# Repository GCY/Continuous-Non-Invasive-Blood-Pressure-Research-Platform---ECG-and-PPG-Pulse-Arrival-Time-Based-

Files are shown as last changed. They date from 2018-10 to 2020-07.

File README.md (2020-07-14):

# Continuous Non-Invasive Blood Pressure Research Platform - ECG and PPG Pulse Arrival Time Based
This project is cuffless cNIBP research platform with ECG(two-electrode, without Right Leg Drive(RLD) ) and PPG(MAX3010x),  the Pulse Arrival Time (PAT) using ECG and PPG signal, measure the time delay(∆t) between QRS-Complex of the ECG signal and any one systolic peak of the PPG signal.

<p align="center">
 
</p>

## Hardware

### V4

coming soon...

- STM32F405
- ECG : INA333+AD8669(without RLD)
- Electrode : PCB Pads and NeuroSky EEG dry 6mm electrode(Pinhole PAD1 & PAD2) [NeuroSky](http://neurosky.com)
- PPG : LArm
- LCM : 128x64 SSD1306
- OUTPUT : USB-FS VCP
- Charger : BQ24014

### V3

- STM32F405
- ECG : INA827+LM324PWR(without RLD)
- Electrode : PCB Pads and NeuroSky EEG dry 6mm electrode(Pinhole PAD1 & PAD2) [NeuroSky](http://neurosky.com)
- PPG : LArm
- LCM : 128x64 SSD1306
- OUTPUT : USB-FS VCP
- Charger : TP4056*

#### Note
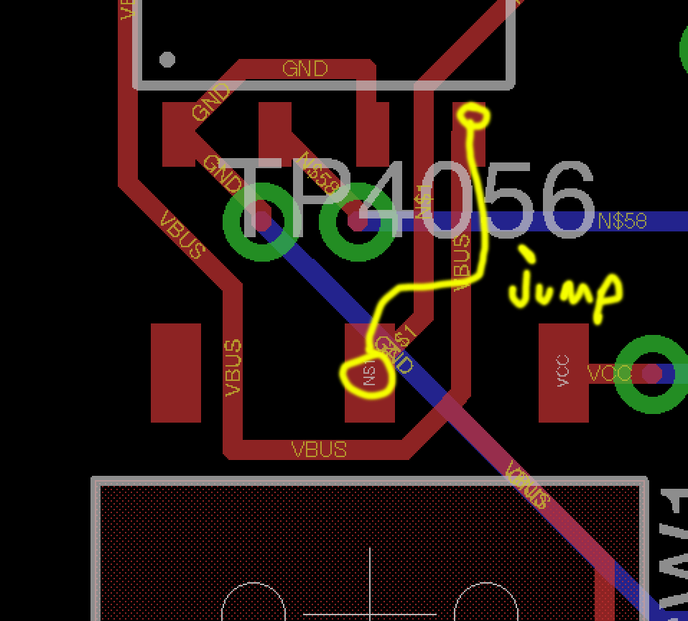
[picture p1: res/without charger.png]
- TP4056 have mV level peak-to-peak noise... so, jump VBUS to switch... 
- Replace D1 to 0R resistor, reduce LDO VDDA noise.
- Unplug the NB AC adapter.

</br>



### V1
- STM32F407
- ECG : INA827+LM324PWR(without RLD)
- Electrode : PCB Pads
- PPG : LArm and RArm
- LCM : 128x64 SSD1306
- OUTPUT : UART

## Firmware
This firmware only for testing, includes USB-FS VCP, Max3010x Spo2 algorithm, PPG and ECG signal oscilloscope display.</br>

 - cd ./firmware/stm32f405/src/
 - make
 - load elf file
 - run
## Software
[wxECGAnalyzer](https://github.com/GCY/wxECGAnalyzer) is a QRS-Complex ECG signal process tool and QRS-Complex detection algorithm validation tools, [Pulse Oximeter MAX3010X](https://github.com/GCY/Pulse-Oximeter-with-MAX3010X) is a Spo2 signal process and r-ratio finetune tool, combining the two tools, could implement the PAT-BP regression algorithm.

</br>

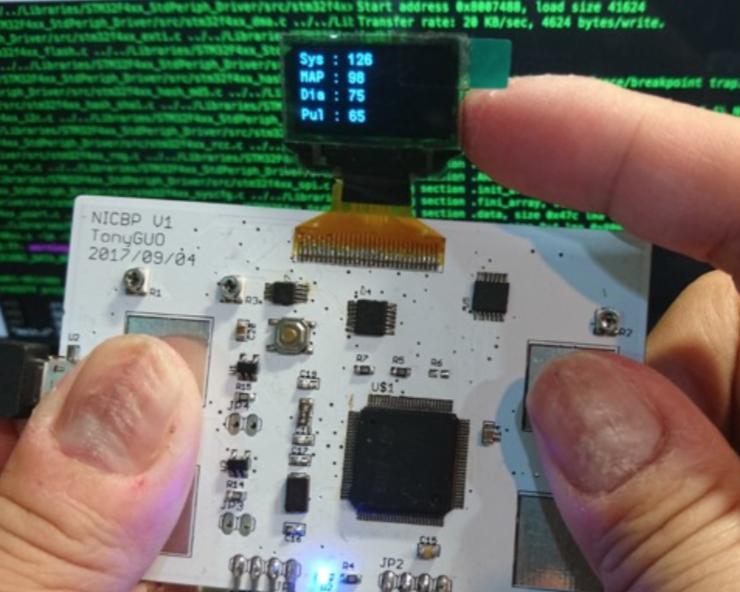
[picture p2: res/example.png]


## Pulse Arrival Time Calculate

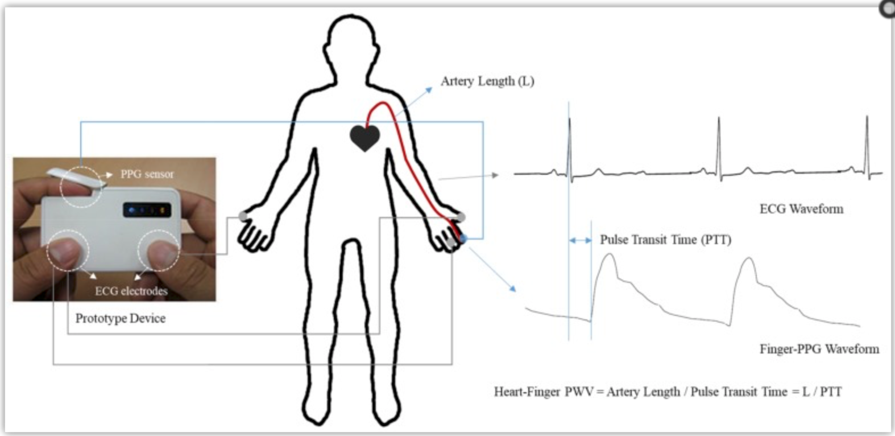
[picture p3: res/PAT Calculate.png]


## What's cuff-less blood pressure monitor and difference between Pulse Arrival Time(PAT) and Pulse Transit Time(PTT)
In cuffless non-invasive blood pressure monitor field, we with the accurate calibration of PAT to BP, beat-to-beat BP can be estimated from PAT. On the basis of the theoretical relationship between PAT and BP and their experimental or empirical relationship, various models that correlate PAT with BP have been established.</br>
</br>
PAT and BP with Regression: </br>
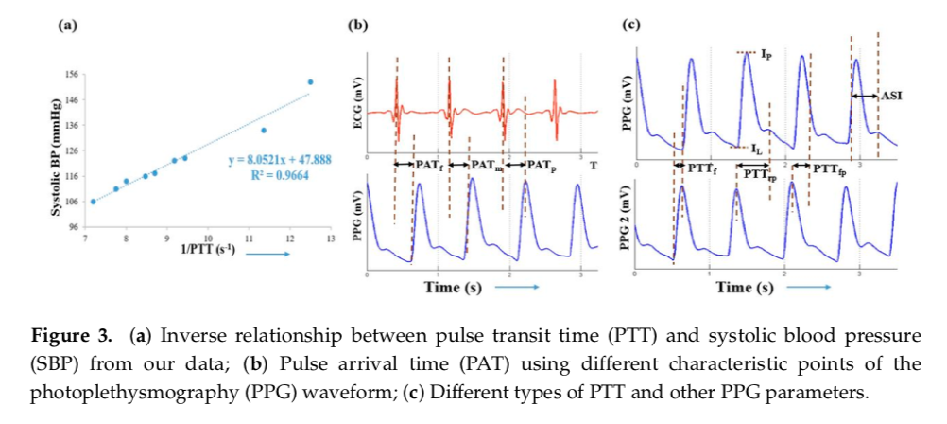
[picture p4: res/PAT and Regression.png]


</br>
</br>
Pulse transit time (PTT) is the time it takes for the pressure or flow wave to propagate between two arterial sites.
PTT measured as the time delay between invasive proximal and distal blood pressure or flow, and PTT(propagate time) can be converted to Pulse Wave Velocity(PWV is speed unit).

the most used is the R-wave(QRS Complex) in the electrocardiogram (ECG) and combine pulsemeter(piezo or PPG), leading to the so called pulse arrival time (PAT). 
PAT is not exactly the PTT, as it includes the time interval between ventricular depolarization and the opening of the aortic valve which is known as pre-ejection period (PEP) and it varies beat-to-beat.

Most efforts have employed the time delay between ECG and finger photoplethysmography (PPG) waveforms as a convenient surrogate of PTT. 

However, these conventional pulse arrival time (PAT) measurements include the pre-ejection period (PEP) and the time delay through small,
muscular arteries and may thus be an unreliable marker of BP.

Shortcoming is that PAT includes the pre-ejection period (PEP) in addition to PTT. 
Since the PEP component depends on the electromechanical functioning of the heart, it can change independently of PTT and thus BP. 

Because the ECG QRS-Complex is not the starting point for blood to actually enter the radial artery, it is a biopotential to depolarization of the sinus node

</br>

## This project only for research

</br>

(https://www.youtube.com/watch?v=RtydQm8okKk)

</br>

## Reference :
- [1] Continuous Blood Pressure Measurement from Invasive to Unobtrusive: Celebration of 200th Birth Anniversary of Carl Ludwig</br>
- [2] Cuff-Less and Continuous Blood Pressure Monitoring: A Methodological Review</br>
- [3] https://www.egr.msu.edu/classes/ece480/capstone/spring13/group03/documents.html
- [4] Cho, J., & Baek, H. J. (2020). A Comparative Study of Brachial–Ankle Pulse Wave Velocity and Heart–Finger Pulse Wave Velocity in Korean Adults. Sensors, 20(7), 2073.
 
LICENSE
-------

MIT License

Copyright (c) 2020 Tony Guo

Permission is hereby granted, free of charge, to any person obtaining a copy
of this software and associated documentation files (the "Software"), to deal
in the Software without restriction, including without limitation the rights
to use, copy, modify, merge, publish, distribute, sublicense, and/or sell
copies of the Software, and to permit persons to whom the Software is
furnished to do so, subject to the following conditions:

The above copyright notice and this permission notice shall be included in all
copies or substantial portions of the Software.

THE SOFTWARE IS PROVIDED "AS IS", WITHOUT WARRANTY OF ANY KIND, EXPRESS OR
IMPLIED, INCLUDING BUT NOT LIMITED TO THE WARRANTIES OF MERCHANTABILITY,
FITNESS FOR A PARTICULAR PURPOSE AND NONINFRINGEMENT. IN NO EVENT SHALL THE
AUTHORS OR COPYRIGHT HOLDERS BE LIABLE FOR ANY CLAIM, DAMAGES OR OTHER
LIABILITY, WHETHER IN AN ACTION OF CONTRACT, TORT OR OTHERWISE, ARISING FROM,
OUT OF OR IN CONNECTION WITH THE SOFTWARE OR THE USE OR OTHER DEALINGS IN THE
SOFTWARE.

OSHW Certification
-------

https://certification.oshwa.org/tw000003.html

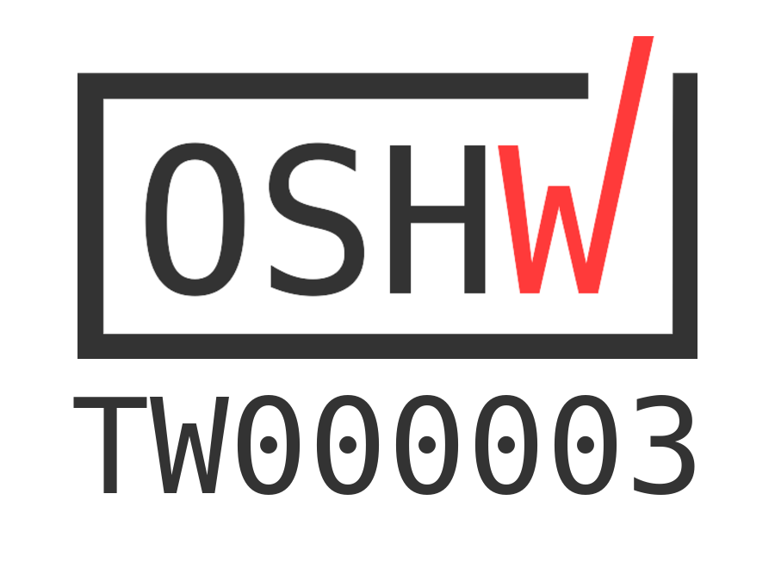
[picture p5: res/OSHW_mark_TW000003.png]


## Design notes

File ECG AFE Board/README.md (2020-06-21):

# ECG Analog-Front-End Design

two electrode ECG without RLD

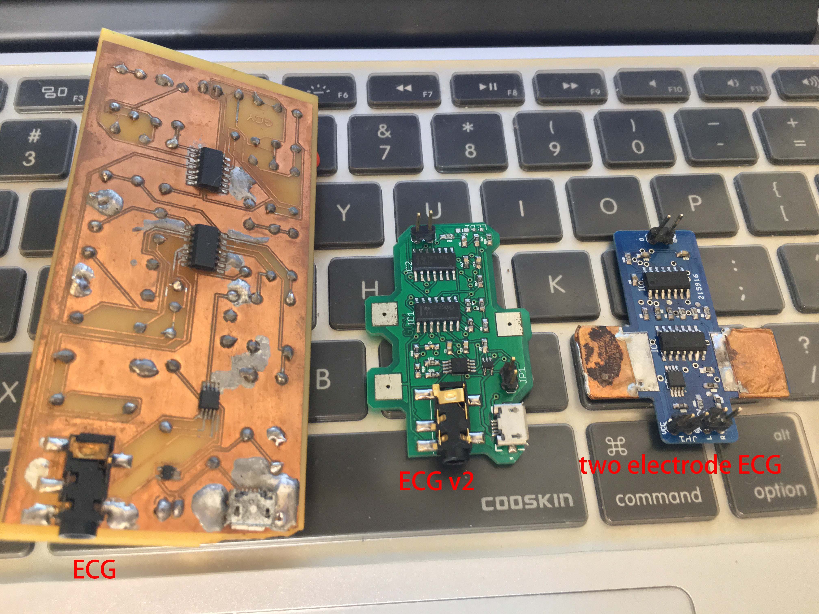
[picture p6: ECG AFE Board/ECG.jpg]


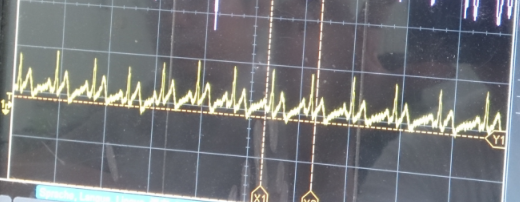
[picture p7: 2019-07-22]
res/ecg osc.png

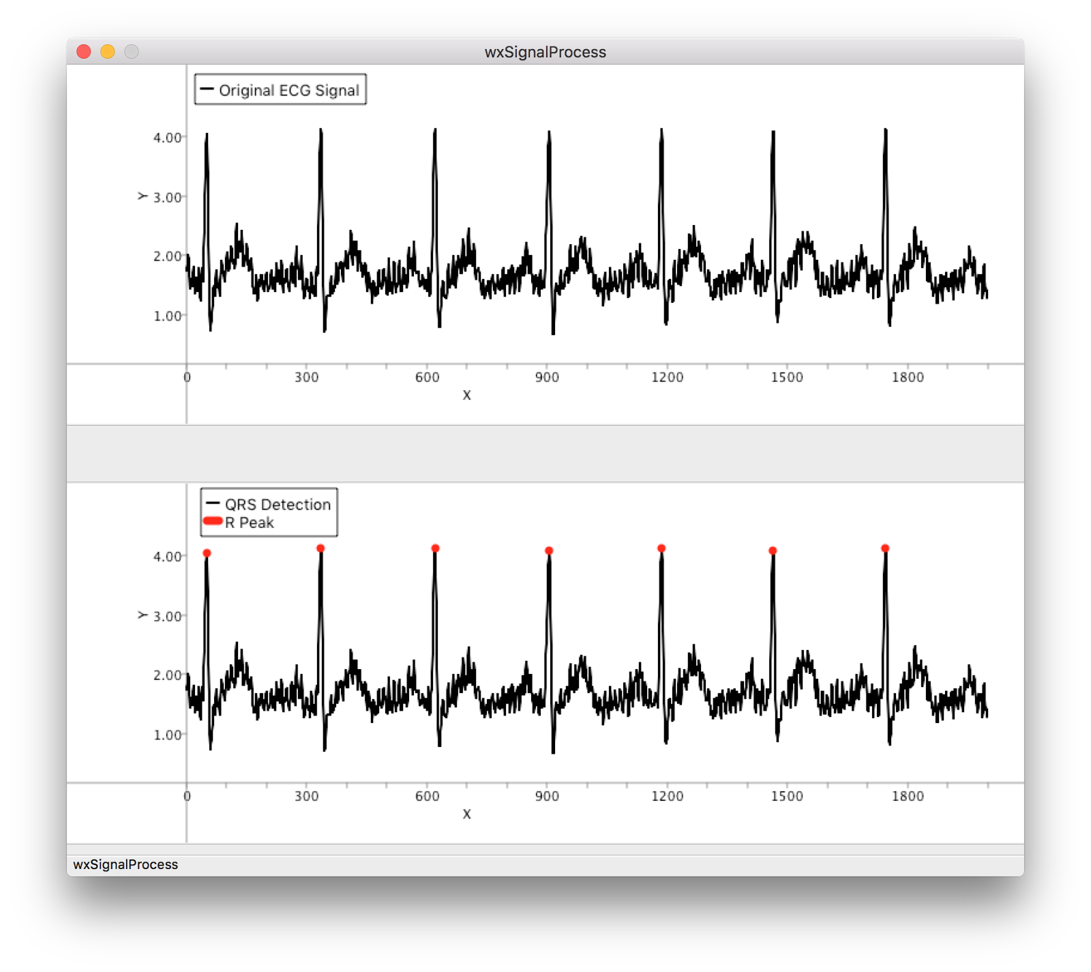
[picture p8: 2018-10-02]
res/QRS Complex Detect.png

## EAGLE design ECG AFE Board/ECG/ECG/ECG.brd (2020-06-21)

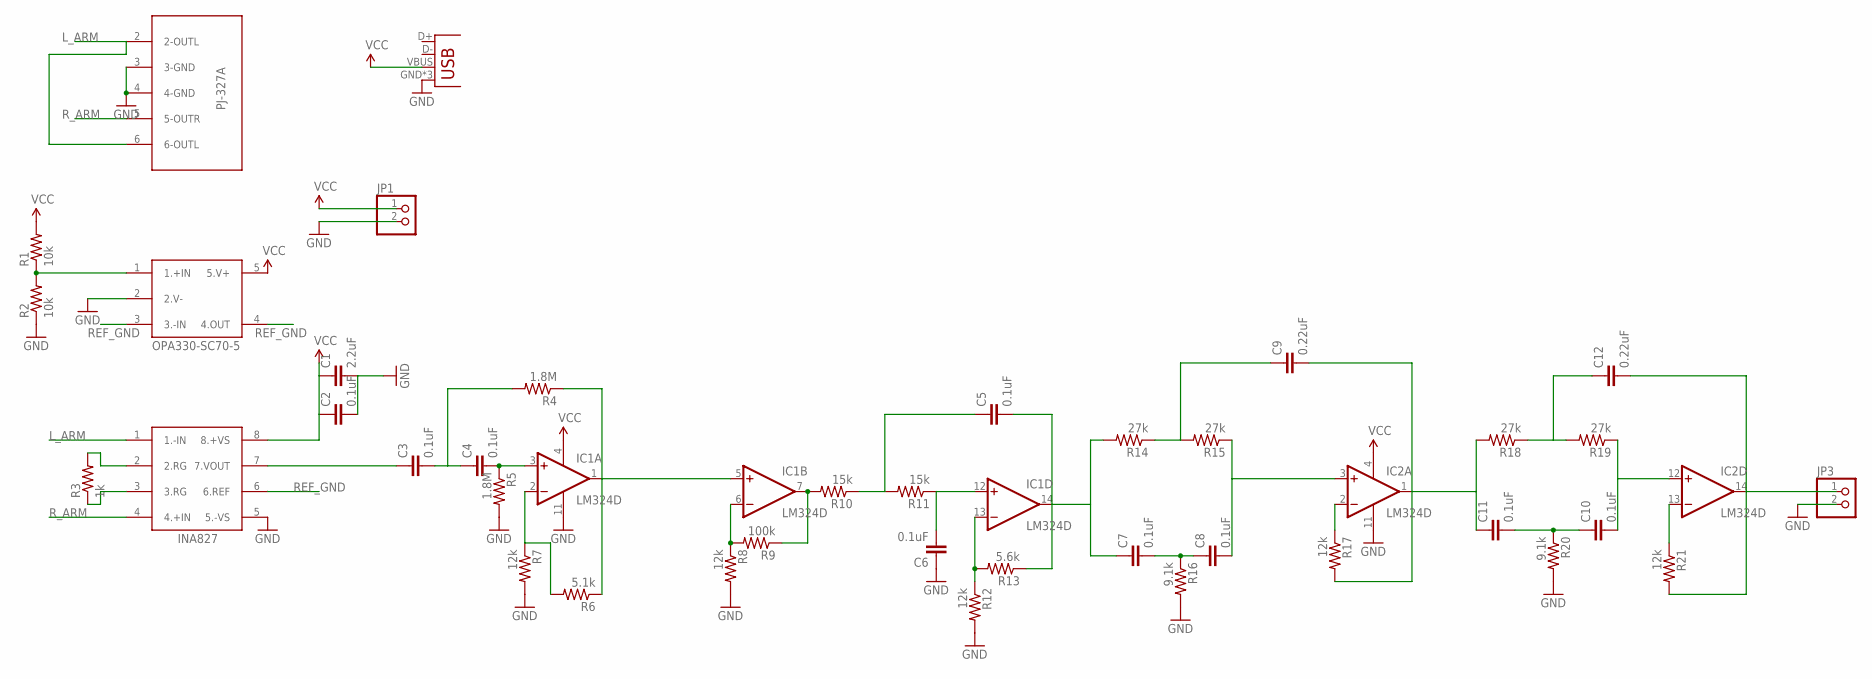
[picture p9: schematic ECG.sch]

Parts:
C1: 2.2uF; CAP-PTH-LARGE
C2, C3, C4, C5, C6, C7, C8, C10, C11: 0.1uF; CAP-PTH-LARGE
C9, C12: 0.22uF; CAP-PTH-LARGE
IC1, IC2: LM324D; SO14
JP1, JP3: PINHD-1X2; 1X02
JP2: USB-MICROB
R1, R2: 10k; AXIAL-0.4
R3: 1k; AXIAL-0.4
R4, R5: 1.8M; AXIAL-0.4
R6: 5.1k; AXIAL-0.4
R7, R8, R12, R17, R21: 12k; AXIAL-0.4
R9: 100k; AXIAL-0.4
R10, R11: 15k; AXIAL-0.4
R13: 5.6k; AXIAL-0.4
R14, R15, R18, R19: 27k; AXIAL-0.4
R16, R20: 9.1k; AXIAL-0.4
U$1: OPA330-SC70-5
U$2: INA827
U$3: PJ-327A

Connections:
GND: C1.2, C2.2, C6.1, IC1.11 (V-), IC2.11 (V-), JP1.2, JP2.GND, JP2.MT1 (GND), JP2.MT2 (GND), JP3.2, R2.P$1 (1), R5.P$2 (2), R7.P$2 (2), R8.P$2 (2), R12.P$2 (2), R16.P$2 (2), R20.P$2 (2), U$1.2 (2.V-), U$2.5 (5.-VS), U$3.3 (3-GND), U$3.4 (4-GND)
L_ARM: U$2.1 (1.-IN), U$3.2 (2-OUTL), U$3.6 (6-OUTL)
unnamed: R1.P$1 (1), R2.P$2 (2), U$1.1 (1.+IN)
unnamed: R3.P$2 (2), U$2.2 (2.RG)
unnamed: R3.P$1 (1), U$2.3 (3.RG)
unnamed: C4.2, IC1.3 (+IN), R5.P$1 (1)
unnamed: C3.1, U$2.7 (7.VOUT)
unnamed: C3.2, C4.1, R4.P$2 (2)
unnamed: IC1.1 (OUT), IC1.5 (+IN), R4.P$1 (1), R6.P$1 (1)
unnamed: IC1.2 (-IN), R6.P$2 (2), R7.P$1 (1)
unnamed: C5.1, R10.P$1 (1), R11.P$2 (2)
unnamed: IC1.6 (-IN), R8.P$1 (1), R9.P$2 (2)
unnamed: IC1.7 (OUT), R9.P$1 (1), R10.P$2 (2)
unnamed: C6.2, IC1.12 (+IN), R11.P$1 (1)
unnamed: C5.2, C7.1, IC1.14 (OUT), R13.P$1 (1), R14.P$2 (2)
unnamed: IC1.13 (-IN), R12.P$1 (1), R13.P$2 (2)
unnamed: C9.1, R14.P$1 (1), R15.P$2 (2)
unnamed: C8.2, IC2.3 (+IN), R15.P$1 (1)
unnamed: C7.2, C8.1, R16.P$1 (1)
unnamed: IC2.2 (-IN), R17.P$1 (1)
unnamed: C9.2, C11.1, IC2.1 (OUT), R17.P$2 (2), R18.P$2 (2)
unnamed: IC2.13 (-IN), R21.P$1 (1)
unnamed: C10.1, C11.2, R20.P$1 (1)
unnamed: C10.2, IC2.12 (+IN), R19.P$1 (1)
unnamed: C12.1, R18.P$1 (1), R19.P$2 (2)
unnamed: C12.2, IC2.14 (OUT), JP3.1, R21.P$2 (2)
REF_GND: U$1.3 (3.-IN), U$1.4 (4.OUT), U$2.6 (6.REF)
R_ARM: U$2.4 (4.+IN), U$3.5 (5-OUTR)
VCC: C1.1, C2.1, IC1.4 (V+), IC2.4 (V+), JP1.1, JP2.VBUS, R1.P$2 (2), U$1.5 (5.V+), U$2.8 (8.+VS)

Board: 2 copper layers, 41 parts (0 on the bottom side), 29 nets, no tracks yet.

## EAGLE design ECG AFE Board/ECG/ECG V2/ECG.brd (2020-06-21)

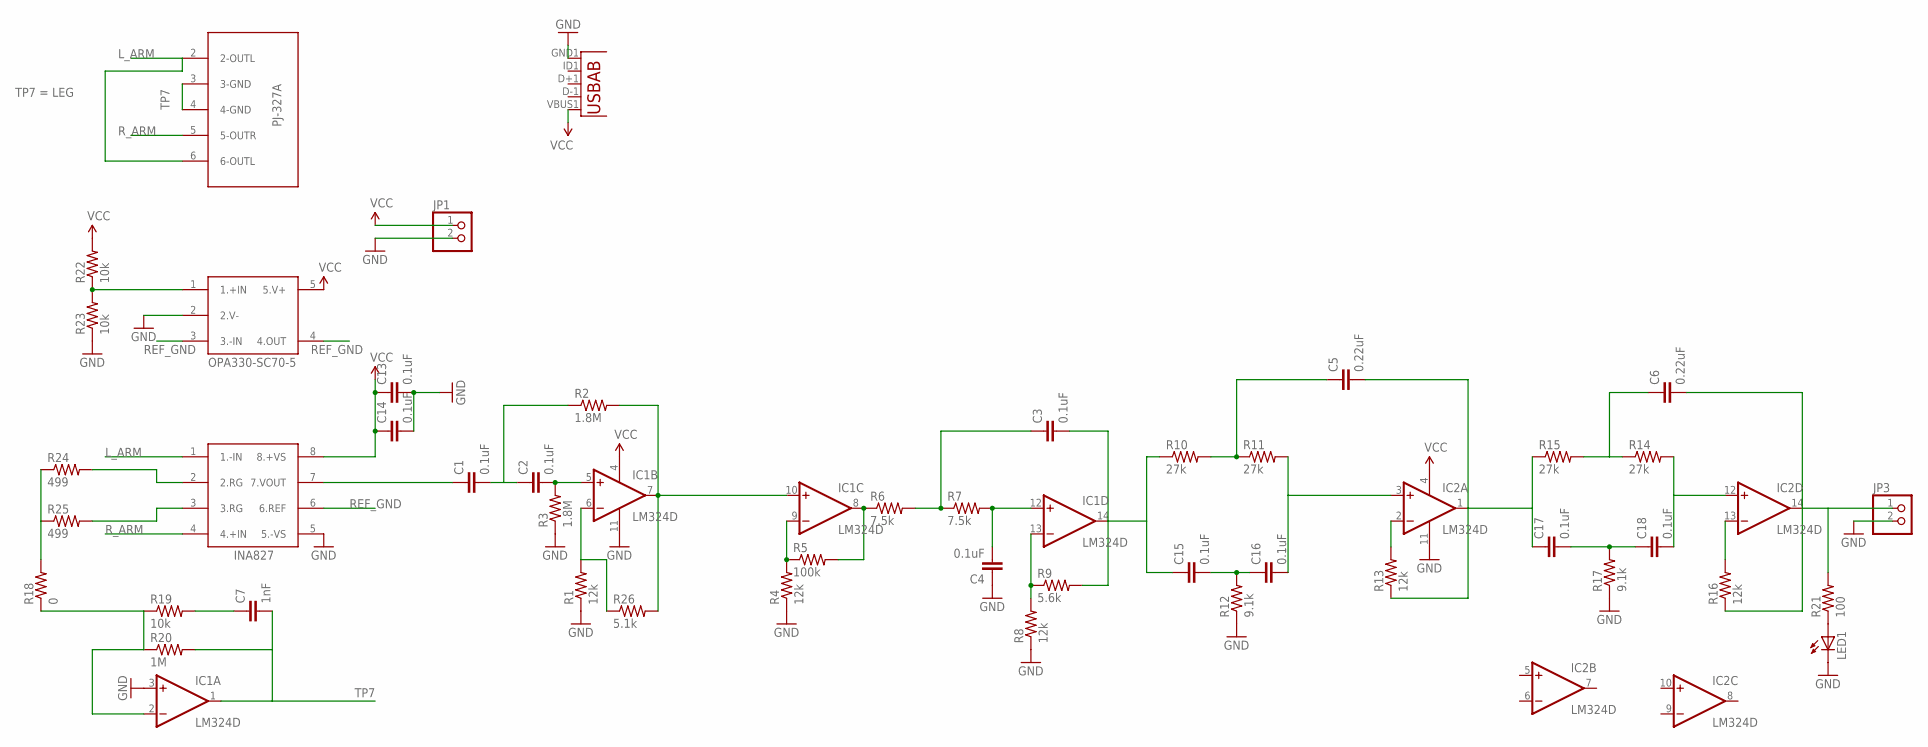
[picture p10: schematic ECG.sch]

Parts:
C1, C2, C3, C4, C13, C14, C15, C16, C17, C18: 0.1uF; 0603-CAP
C5, C6: 0.22uF; 0603-CAP
C7: 1nF; 0603-CAP
IC1, IC2: LM324D; SO14
JP1, JP3: PINHD-1X2; 1X02
LED1: LEDCHIPLED_0603; CHIPLED_0603
R1, R4, R8, R13, R16: 12k; 0603-RES
R2, R3: 1.8M; 0603-RES
R5: 100k; 0603-RES
R6, R7: 7.5k; 0603-RES
R9: 5.6k; 0603-RES
R10, R11, R14, R15: 27k; 0603-RES
R12, R17: 9.1k; 0603-RES
R18: 0; 0603-RES
R19, R22, R23: 10k; 0603-RES
R20: 1M; 0603-RES
R21: 100; 0603-RES
R24, R25: 499; 0603-RES
R26: 5.1k; 0603-RES
U1: USB""; USB-MICRO-SMD
U$1: OPA330-SC70-5
U$2: INA827
U$3: PJ-327A

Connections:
GND: C4.1, C13.2, C14.2, IC1.3 (+IN), IC1.11 (V-), IC2.11 (V-), JP1.2, JP3.2, LED1.C, R1.1, R3.1, R4.1, R8.1, R12.1, R17.1, R23.1, U1.GND1 (GND), U$1.2 (2.V-), U$2.5 (5.-VS)
L_ARM: U$2.1 (1.-IN), U$3.2 (2-OUTL), U$3.6 (6-OUTL)
unnamed: R22.1, R23.2, U$1.1 (1.+IN)
unnamed: R24.2, U$2.2 (2.RG)
unnamed: R25.2, U$2.3 (3.RG)
unnamed: C2.2, IC1.5 (+IN), R3.2
unnamed: C1.1, U$2.7 (7.VOUT)
unnamed: C1.2, C2.1, R2.1
unnamed: IC1.7 (OUT), IC1.10 (+IN), R2.2, R26.2
unnamed: IC1.6 (-IN), R1.2, R26.1
unnamed: C3.1, R6.2, R7.1
unnamed: IC1.9 (-IN), R4.2, R5.1
unnamed: IC1.8 (OUT), R5.2, R6.1
unnamed: C4.2, IC1.12 (+IN), R7.2
unnamed: C3.2, C15.1, IC1.14 (OUT), R9.2, R10.1
unnamed: IC1.13 (-IN), R8.2, R9.1
unnamed: C5.1, R10.2, R11.1
unnamed: C16.2, IC2.3 (+IN), R11.2
unnamed: C15.2, C16.1, R12.2
unnamed: IC2.2 (-IN), R13.2
unnamed: C5.2, C17.1, IC2.1 (OUT), R13.1, R15.1
unnamed: IC2.13 (-IN), R16.2
unnamed: C17.2, C18.1, R17.2
unnamed: C18.2, IC2.12 (+IN), R14.2
unnamed: C6.1, R14.1, R15.2
unnamed: C6.2, IC2.14 (OUT), JP3.1, R16.1, R21.2
unnamed: R18.2, R24.1, R25.1
unnamed: IC1.2 (-IN), R18.1, R19.1, R20.1
unnamed: C7.1, R19.2
unnamed: LED1.A, R21.1
REF_GND: U$1.3 (3.-IN), U$1.4 (4.OUT), U$2.6 (6.REF)
R_ARM: U$2.4 (4.+IN), U$3.5 (5-OUTR)
TP7: C7.2, IC1.1 (OUT), R20.2, U$3.3 (3-GND), U$3.4 (4-GND)
VCC: C13.1, C14.1, IC1.4 (V+), IC2.4 (V+), JP1.1, R22.2, U1.VBUS1 (VBUS), U$1.5 (5.V+), U$2.8 (8.+VS)

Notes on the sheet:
TP7 = LEG

Board: 2 copper layers, 48 parts (19 on the bottom side), 34 nets, no tracks yet.

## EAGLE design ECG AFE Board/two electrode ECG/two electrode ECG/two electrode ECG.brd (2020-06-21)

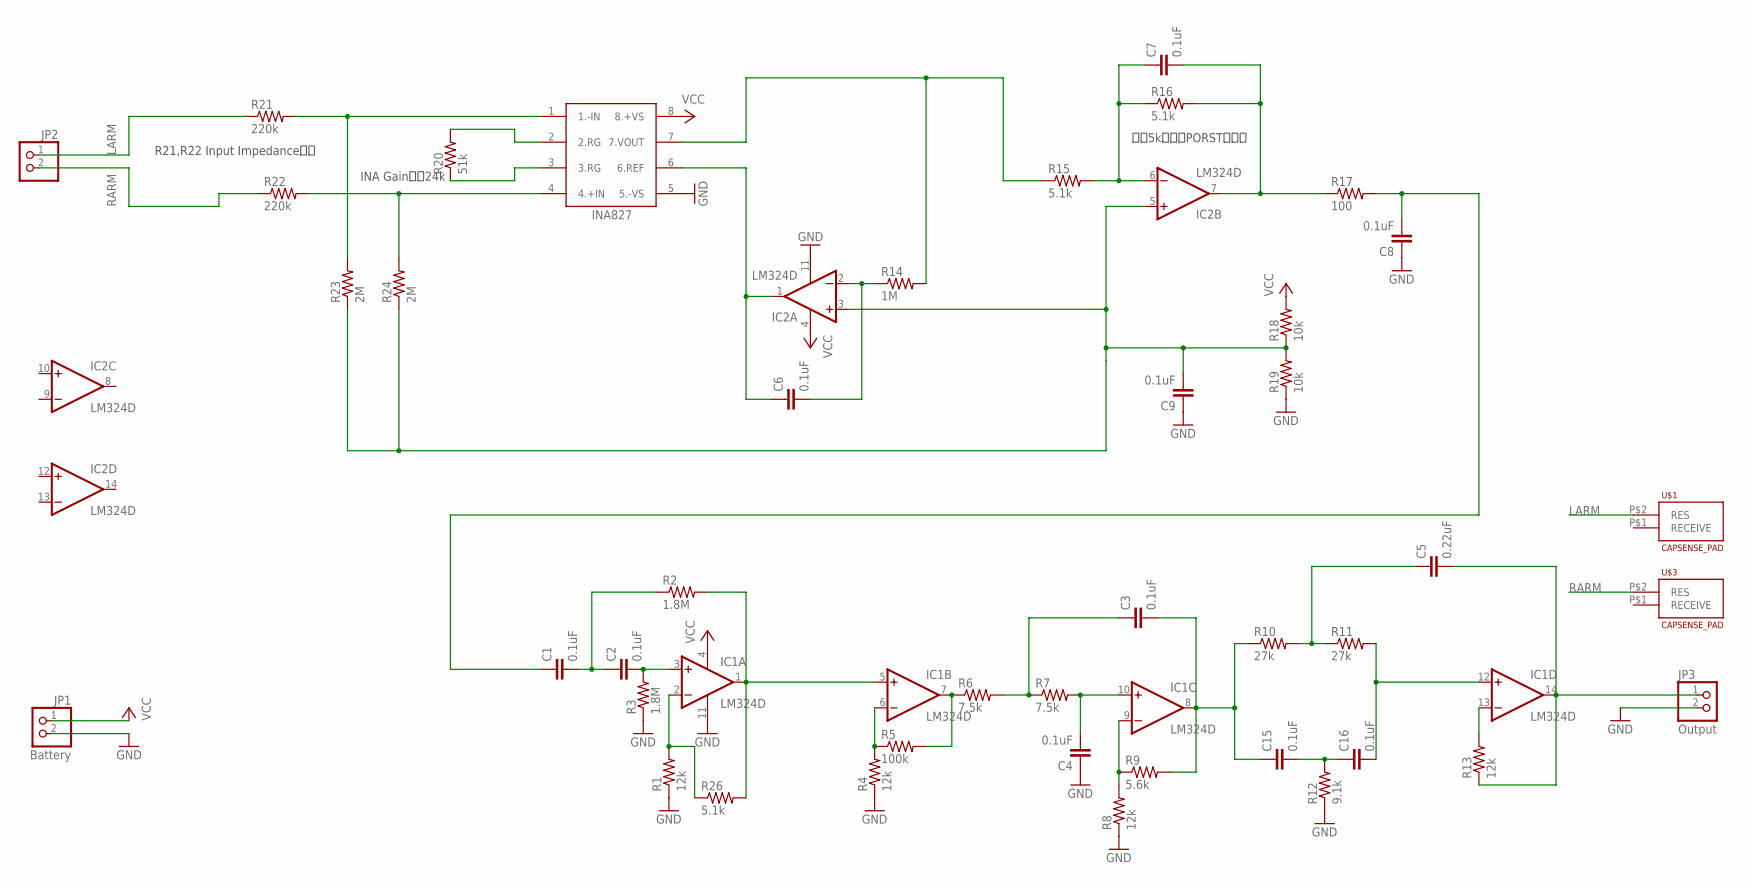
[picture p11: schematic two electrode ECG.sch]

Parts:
C1, C2, C3, C4, C6, C7, C8, C9, C15, C16: 0.1uF; 0603-CAP
C5: 0.22uF; 0603-CAP
IC1, IC2: LM324D; SO14
JP1: Battery; 1X02
JP2: PINHD-1X2; 1X02
JP3: Output; 1X02
R1, R4, R8, R13: 12k; 0603-RES
R2, R3: 1.8M; 0603-RES
R5: 100k; 0603-RES
R6, R7: 7.5k; 0603-RES
R9: 5.6k; 0603-RES
R10, R11: 27k; 0603-RES
R12: 9.1k; 0603-RES
R14: 1M; 0603-RES
R15, R16, R26: 5.1k; 0603-RES
R17: 100; 0603-RES
R18, R19: 10k; 0603-RES
R20: 51k; 0603-RES
R21, R22: 220k; 0603-RES
R23, R24: 2M; 0603-RES
U$1, U$3: CAPSENSE_PAD
U$2: INA827

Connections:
GND: C4.1, C8.1, C9.1, IC1.11 (V-), IC2.11 (V-), JP1.2, JP3.2, R1.1, R3.1, R4.1, R8.1, R12.1, R19.1, U$2.5 (5.-VS)
LARM: JP2.1, R21.1, U$1.P$2 (RES)
unnamed: R20.2, U$2.2 (2.RG)
unnamed: C6.2, IC2.2 (-IN), R14.1
unnamed: R14.2, R15.1, U$2.7 (7.VOUT)
unnamed: C2.2, IC1.3 (+IN), R3.2
unnamed: R21.2, R23.2, U$2.1 (1.-IN)
unnamed: C1.2, C2.1, R2.1
unnamed: IC1.1 (OUT), IC1.5 (+IN), R2.2, R26.2
unnamed: IC1.2 (-IN), R1.2, R26.1
unnamed: C3.1, R6.2, R7.1
unnamed: IC1.6 (-IN), R4.2, R5.1
unnamed: IC1.7 (OUT), R5.2, R6.1
unnamed: C4.2, IC1.10 (+IN), R7.2
unnamed: C3.2, C15.1, IC1.8 (OUT), R9.2, R10.1
unnamed: IC1.9 (-IN), R8.2, R9.1
unnamed: C5.1, R10.2, R11.1
unnamed: C16.2, IC1.12 (+IN), R11.2
unnamed: C15.2, C16.1, R12.2
unnamed: IC1.13 (-IN), R13.2
unnamed: C5.2, IC1.14 (OUT), JP3.1, R13.1
unnamed: C6.1, IC2.1 (OUT), U$2.6 (6.REF)
unnamed: C7.1, IC2.6 (-IN), R15.2, R16.1
unnamed: C7.2, IC2.7 (OUT), R16.2, R17.1
unnamed: C1.1, C8.2, R17.2
unnamed: C9.2, IC2.3 (+IN), IC2.5 (+IN), R18.1, R19.2, R23.1, R24.1
unnamed: R20.1, U$2.3 (3.RG)
unnamed: R22.2, R24.2, U$2.4 (4.+IN)
RARM: JP2.2, R22.1, U$3.P$2 (RES)
VCC: IC1.4 (V+), IC2.4 (V+), JP1.1, R18.2, U$2.8 (8.+VS)

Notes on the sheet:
R21,R22 Input Impedance調整
INA Gain調整24k
要改5k，否則PORST會消失

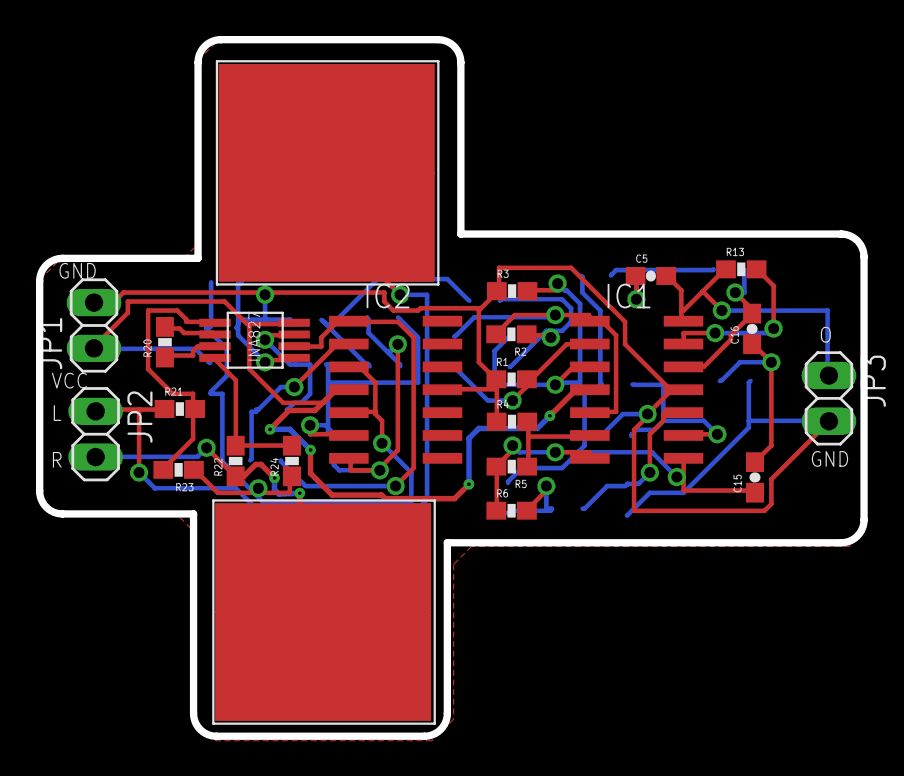
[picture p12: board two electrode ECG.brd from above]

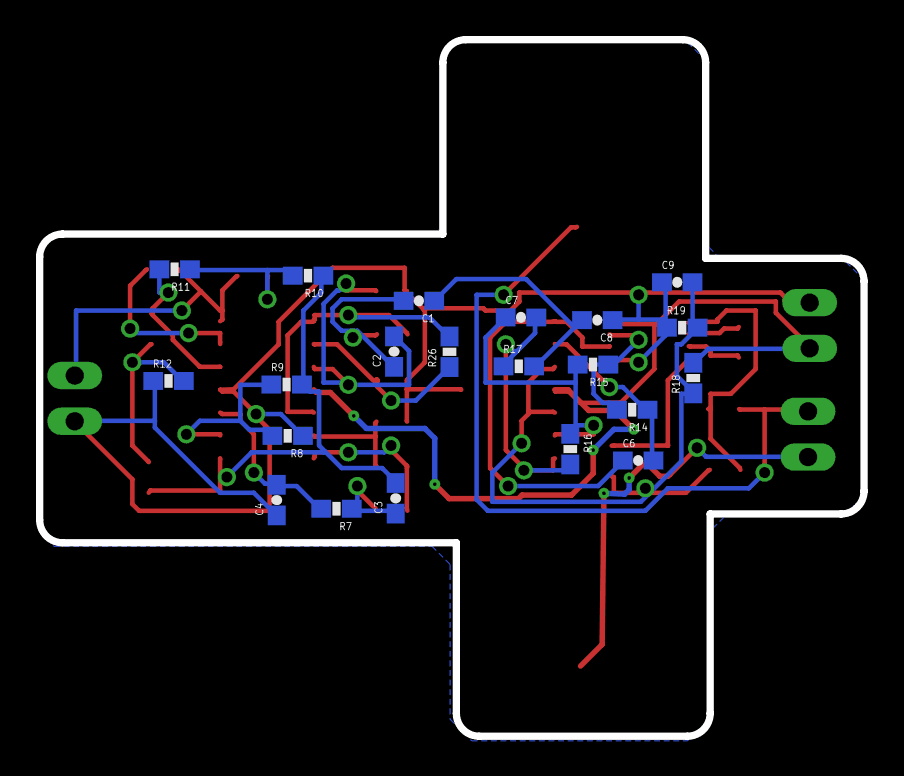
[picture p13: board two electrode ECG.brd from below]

Board: 2 copper layers, 45.8 x 38.7 mm, 44 parts (21 on the bottom side), 30 nets.

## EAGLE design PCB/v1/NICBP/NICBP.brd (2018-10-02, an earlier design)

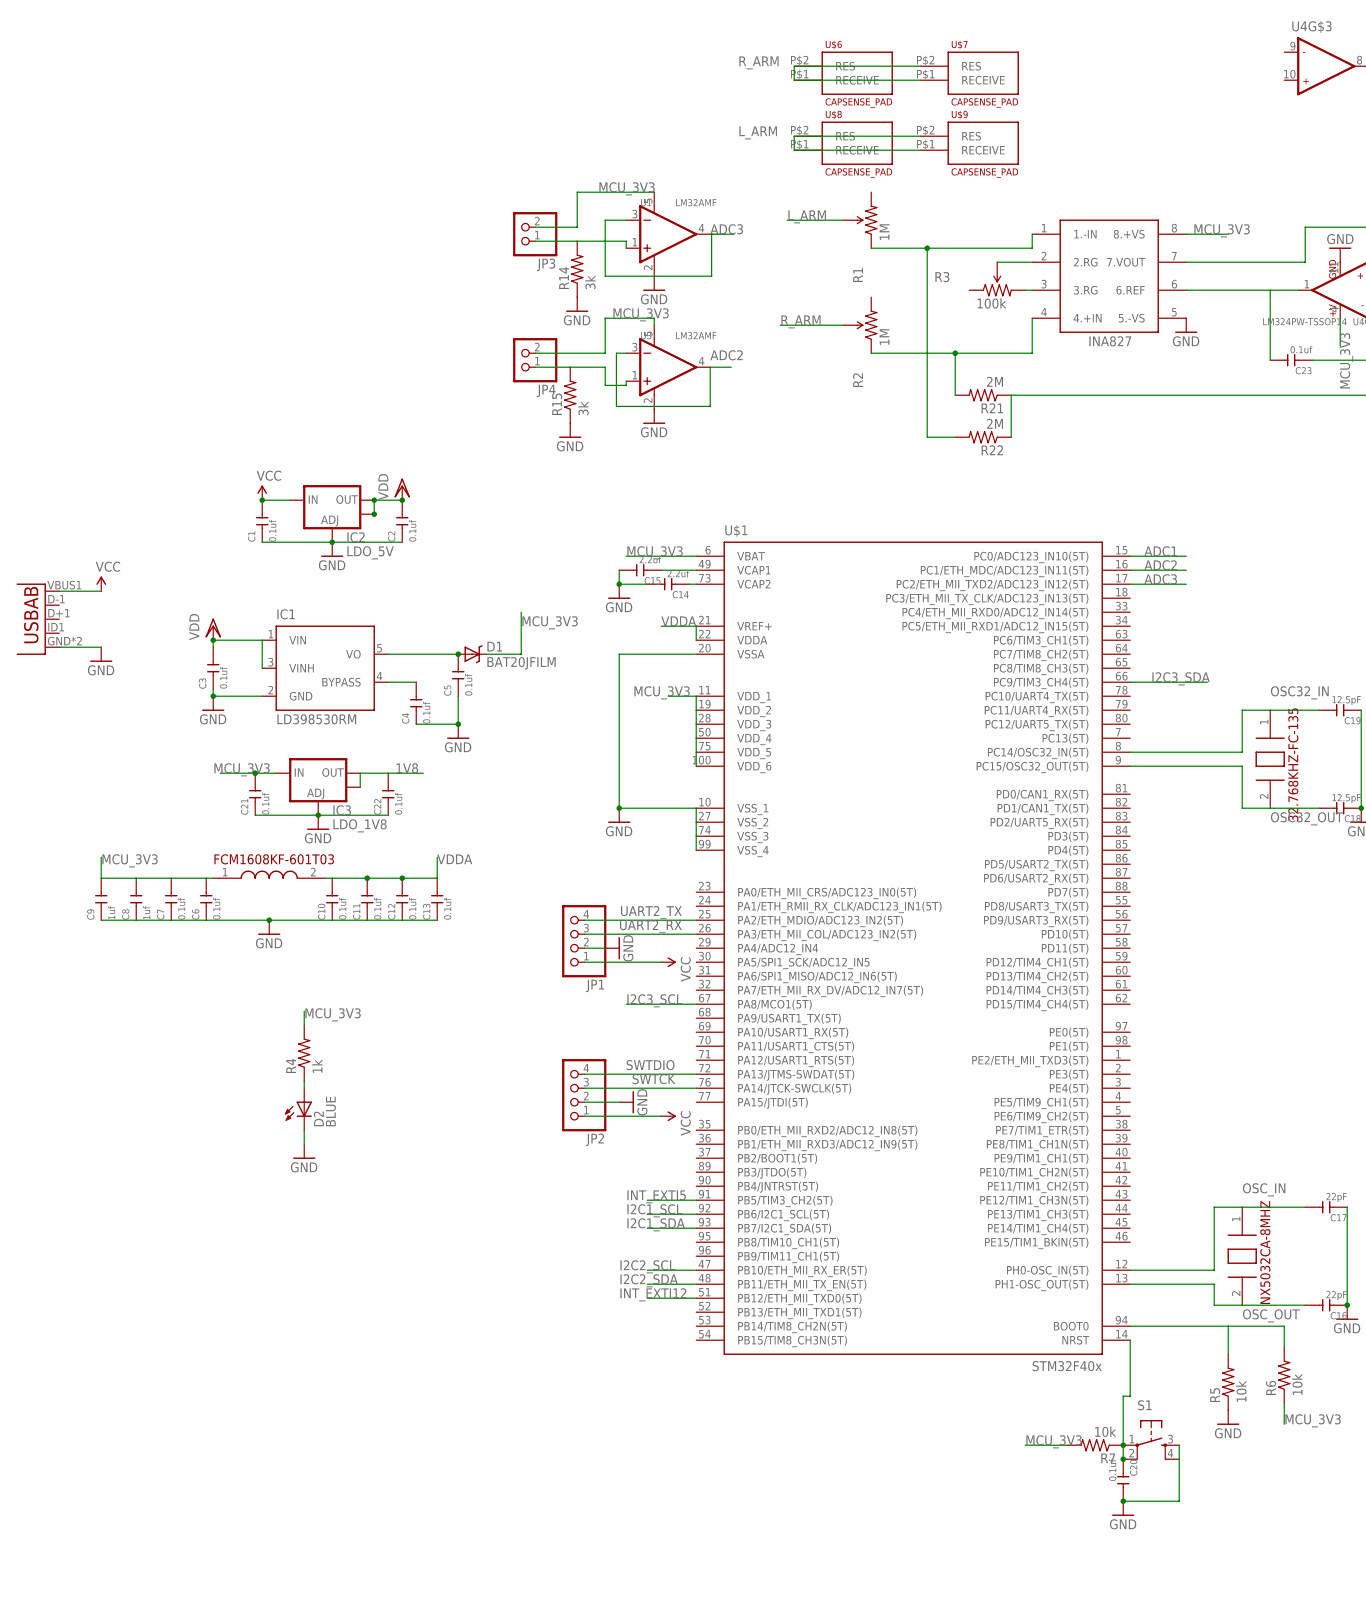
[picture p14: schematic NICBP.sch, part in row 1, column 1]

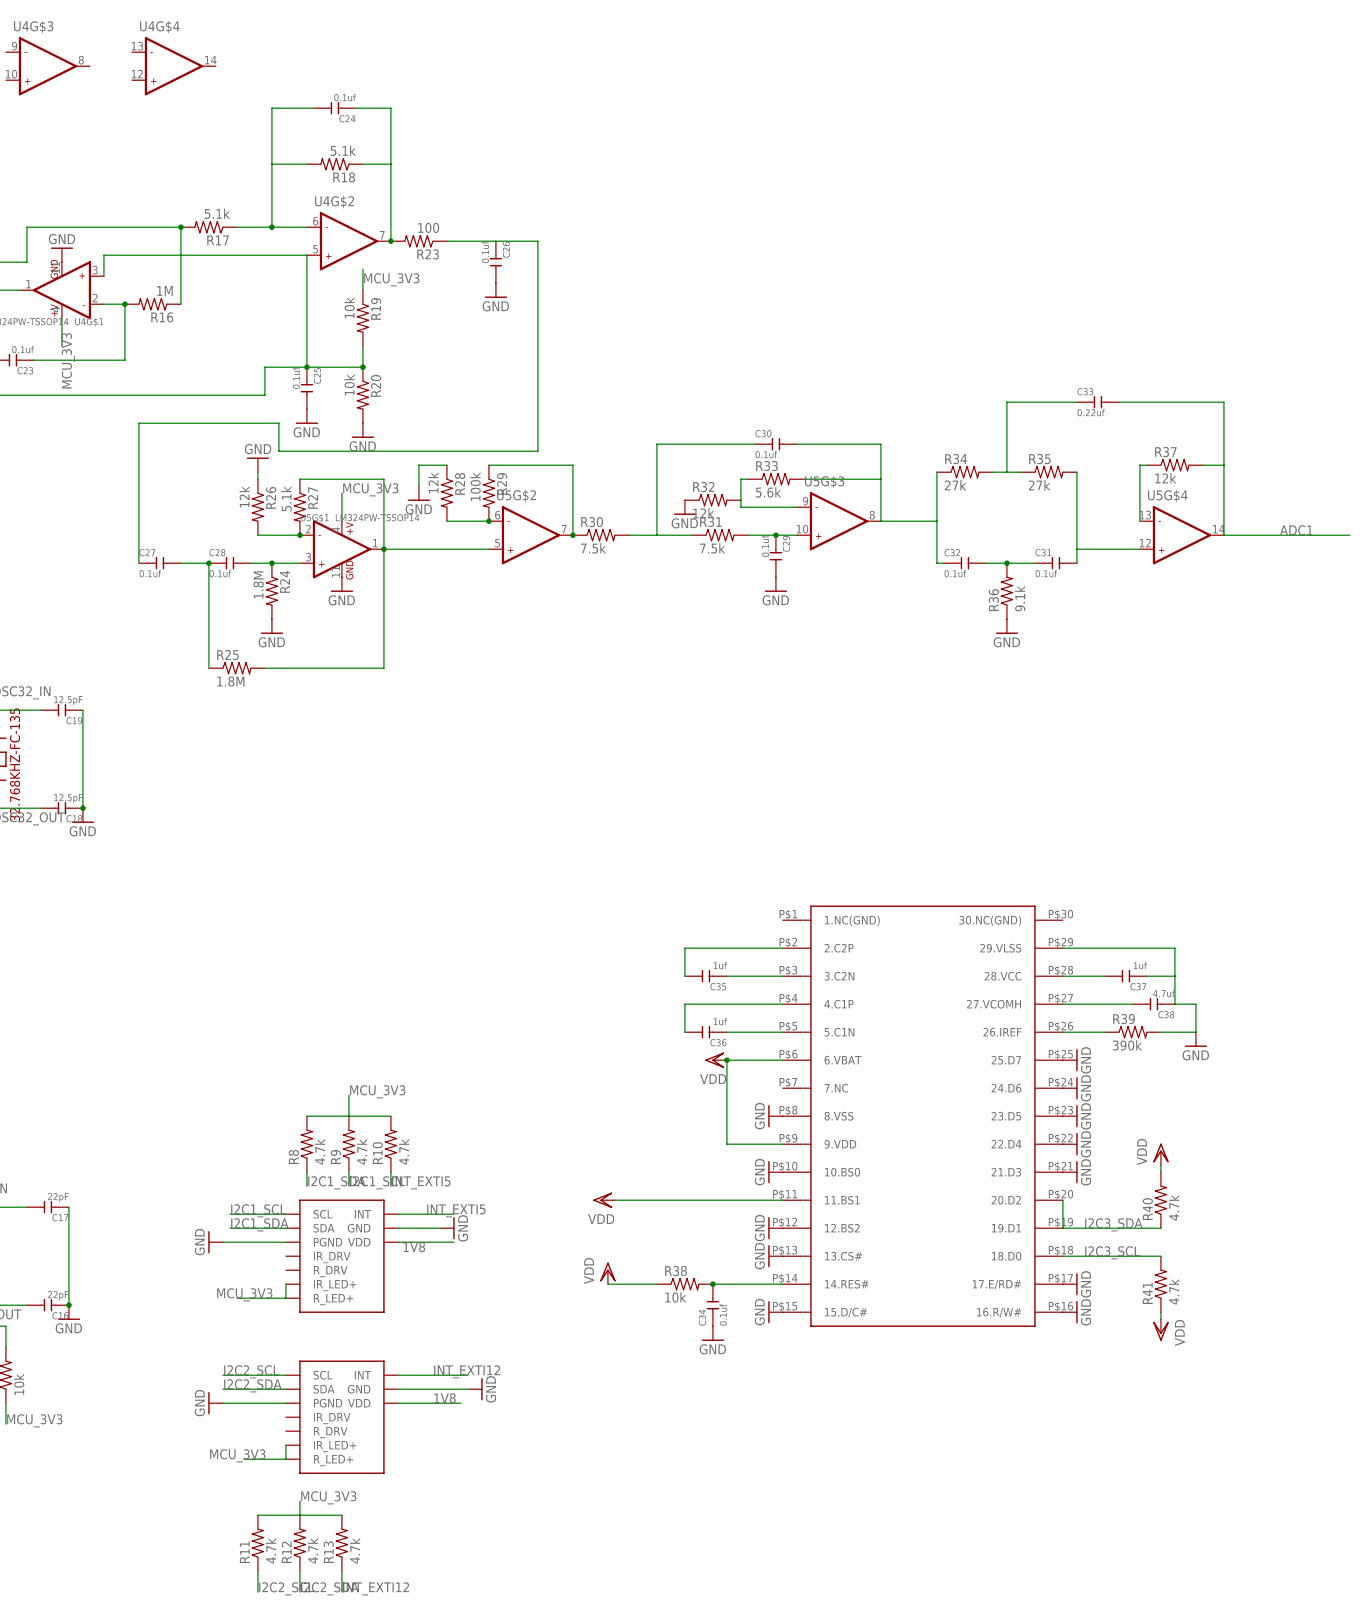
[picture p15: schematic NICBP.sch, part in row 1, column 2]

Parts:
C1, C2, C3, C4, C5, C6, C7, C10, C11, C12, C13, C20, C21, C22, C23, C24, C25, C26, C27, C28, C29, C30, C31, C32, C34: 0.1uf; C0603
C8, C9, C35, C36, C37: 1uf; C0603
C14, C15: 2.2uf; C0603
C16, C17: 22pF; C0603
C18, C19: 12.5pF; C0603
C33: 0.22uf; C0603
C38: 4.7uf; C0603
D1: BAT20JFILM; SOD-323
D2: BLUE; LED-0603
IC1: LD398530RM; SOT23-5L
IC2: LDO_5V; SOT223
IC3: LDO_1V8; SOT223
JP1, JP2: PINHD-1X4; 1X04
JP3, JP4: PINHD-1X2; 1X02
R1, R2: 1M; TRIMPOT_TC33
R3: 100k; TRIMPOT_TC33
R4: 1k; 0603
R5, R6, R7, R19, R20, R38: 10k; 0603
R8, R9, R10, R11, R12, R13, R40, R41: 4.7k; 0603
R14, R15: 3k; 0603
R16: 1M; 0603
R17, R18, R27: 5.1k; 0603
R21, R22: 2M; 0603
R23: 100; 0603
R24, R25: 1.8M; 0603
R26, R28, R32, R37: 12k; 0603
R29: 100k; 0603
R30, R31: 7.5k; 0603
R33: 5.6k; 0603
R34, R35: 27k; 0603
R36: 9.1k; 0603
R39: 390k; 0603
S1: TAC_SWITCHSMD; TACTILE_SWITCH_SMD
U1, U3: LM32AMF; SOT-23-5
U2: USB""; USB-MICRO-SMD
U4, U5: LM324PW-TSSOP14; TSSOP14-0.65-5X4.4MM
U$1: STM32F407V; TQFP100
U$2: NX5032CA-8MHZ
U$3: FCM1608KF-601T03
U$4: 32.768KHZ-FC-135
U$5: INA827
U$6, U$7, U$8, U$9: CAPSENSE_PAD
U$10, U$11: MAX30100
U$12: ER-OLED0.96

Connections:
1V8: C22.2, IC3.2 (OUT), IC3.4 (OUT), U$10.11 (VDD), U$11.11 (VDD)
ADC1: C33.2, R37.2, U5.14 (OUT2), U$1.15 (PC0/ADC123_IN10(5T))
ADC2: U3.3 (IN-), U3.4 (OUT), U$1.16 (PC1/ETH_MDC/ADC123_IN11(5T))
ADC3: U1.3 (IN-), U1.4 (OUT), U$1.17 (PC2/ETH_MII_TXD2/ADC123_IN12(5T))
GND: C1.1, C2.1, C3.1, C4.1, C5.1, C6.1, C7.1, C8.1, C9.1, C10.1, C11.1, C12.1, C13.1, C14.2, C15.2, C16.1, C17.1, C18.1, C19.1, C20.2, C21.1, C22.1, C25.2, C26.2, C29.2, C34.1, C37.1, C38.1, D2.C, IC1.2 (GND), IC2.1 (ADJ), IC3.1 (ADJ), JP1.2, JP2.2, R5.1, R14.1, R15.1, R20.2, R24.2, R26.1, R28.1, R32.1, R36.1, R39.2, S1.3, S1.4, U1.2 (V-), U2.GND, U2.GND1 (GND), U3.2 (V-), U4.11 (GND), U5.11 (GND), U$1.10 (VSS_1), U$1.20 (VSSA), U$1.27 (VSS_2), U$1.74 (VSS_3), U$1.99 (VSS_4), U$5.5 (5.-VS), U$10.4 (PGND), U$10.12 (GND), U$11.4 (PGND), U$11.12 (GND), U$12.P$8 (8.VSS), U$12.P$10 (10.BS0), U$12.P$12 (12.BS2), U$12.P$13 (13.CS#), U$12.P$15 (15.D/C#), U$12.P$16 (16.R/W#), U$12.P$17 (17.E/RD#), U$12.P$21 (21.D3), U$12.P$22 (22.D4), U$12.P$23 (23.D5), U$12.P$24 (24.D6), U$12.P$25 (25.D7), U$12.P$29 (29.VLSS)
I2C1_SCL: R9.1, U$1.92 (PB6/I2C1_SCL(5T)), U$10.2 (SCL)
I2C1_SDA: R8.1, U$1.93 (PB7/I2C1_SDA(5T)), U$10.3 (SDA)
I2C2_SCL: R11.1, U$1.47 (PB10/ETH_MII_RX_ER(5T)), U$11.2 (SCL)
I2C2_SDA: R12.1, U$1.48 (PB11/ETH_MII_TX_EN(5T)), U$11.3 (SDA)
I2C3_SCL: R41.2, U$1.67 (PA8/MCO1(5T)), U$12.P$18 (18.D0)
I2C3_SDA: R40.1, U$1.66 (PC9/TIM3_CH4(5T)), U$12.P$19 (19.D1), U$12.P$20 (20.D2)
INT_EXTI5: R10.1, U$1.91 (PB5/TIM3_CH2(5T)), U$10.13 (INT)
INT_EXTI12: R13.1, U$1.51 (PB12/ETH_MII_TXD0(5T)), U$11.13 (INT)
L_ARM: R1.2 (WIPER), U$8.P$1 (RECEIVE), U$8.P$2 (RES), U$9.P$1 (RECEIVE), U$9.P$2 (RES)
MCU_3V3: C6.2, C7.2, C8.2, C9.2, C21.2, D1.1 (C), IC3.3 (IN), JP3.2, JP4.2, R4.2, R6.1, R7.2, R8.2, R9.2, R10.2, R11.2, R12.2, R13.2, R19.1, U1.5 (V+), U3.5 (V+), U4.4 (+V), U5.4 (+V), U$1.6 (VBAT), U$1.11 (VDD_1), U$1.19 (VDD_2), U$1.28 (VDD_3), U$1.50 (VDD_4), U$1.75 (VDD_5), U$1.100 (VDD_6), U$3.1 (1.IN), U$5.8 (8.+VS), U$10.9 (R_LED+), U$10.10 (IR_LED+), U$11.9 (R_LED+), U$11.10 (IR_LED+)
unnamed: D2.A, R4.1
unnamed: C15.1, U$1.49 (VCAP1)
unnamed: C14.1, U$1.73 (VCAP2)
unnamed: R5.2, R6.2, U$1.94 (BOOT0)
unnamed: C20.1, R7.1, S1.1, S1.2, U$1.14 (NRST)
unnamed: C4.2, IC1.4 (BYPASS)
unnamed: C5.2, D1.2 (A), IC1.5 (VO)
unnamed: R3.3 (CW), U$5.3 (3.RG)
unnamed: JP4.1, R15.2, U3.1 (IN+)
unnamed: JP3.1, R14.2, U1.1 (IN+)
unnamed: R3.2 (WIPER), U$5.2 (2.RG)
unnamed: C23.2, U4.1 (OUT1), U$5.6 (6.REF)
unnamed: R1.1 (CCW), R22.2, U$5.1 (1.-IN)
unnamed: R2.1 (CCW), R21.2, U$5.4 (4.+IN)
unnamed: C23.1, R16.2, U4.2 (-IN1)
unnamed: R16.1, R17.2, U$5.7 (7.VOUT)
unnamed: C24.2, R17.1, R18.2, U4.6 (-IN2)
unnamed: C25.1, R19.2, R20.1, R21.1, R22.1, U4.3 (+IN1), U4.5 (+IN2)
unnamed: C24.1, R18.1, R23.2, U4.7 (OUT2)
unnamed: C26.1, C27.1, R23.1
unnamed: R26.2, R27.2, U5.2 (-IN1)
unnamed: R25.2, R27.1, U5.1 (OUT1), U5.5 (+IN2)
unnamed: C28.2, R24.1, U5.3 (+IN1)
unnamed: C27.2, C28.1, R25.1
unnamed: R28.2, R29.2, U5.6 (-IN2)
unnamed: R29.1, R30.1, U5.7 (OUT2)
unnamed: C30.1, R30.2, R31.1
unnamed: C29.1, R31.2, U5.10 (+IN2)
unnamed: C30.2, C32.1, R33.2, R34.1, U5.8 (OUT2)
unnamed: R32.2, R33.1, U5.9 (-IN2)
unnamed: C33.1, R34.2, R35.1
unnamed: C31.1, C32.2, R36.2
unnamed: C34.2, R38.2, U$12.P$14 (14.RES#)
unnamed: C31.2, R35.2, U5.12 (+IN2)
unnamed: R37.1, U5.13 (-IN2)
unnamed: C35.1, U$12.P$3 (3.C2N)
unnamed: C36.1, U$12.P$5 (5.C1N)
unnamed: C35.2, U$12.P$2 (2.C2P)
unnamed: C36.2, U$12.P$4 (4.C1P)
unnamed: R39.1, U$12.P$26 (26.IREF)
unnamed: C38.2, U$12.P$27 (27.VCOMH)
unnamed: C37.2, U$12.P$28 (28.VCC)
OSC32_IN: C19.2, U$1.8 (PC14/OSC32_IN(5T)), U$4.1 (1.XIN)
OSC32_OUT: C18.2, U$1.9 (PC15/OSC32_OUT(5T)), U$4.2 (2.XIN)
OSC_IN: C17.2, U$1.12 (PH0-OSC_IN(5T)), U$2.1 (1.XIN)
OSC_OUT: C16.2, U$1.13 (PH1-OSC_OUT(5T)), U$2.2 (2.XOUT)
R_ARM: R2.2 (WIPER), U$6.P$1 (RECEIVE), U$6.P$2 (RES), U$7.P$1 (RECEIVE), U$7.P$2 (RES)
SWTCK: JP2.3, U$1.76 (PA14/JTCK-SWCLK(5T))
SWTDIO: JP2.4, U$1.72 (PA13/JTMS-SWDAT(5T))
UART2_RX: JP1.3, U$1.26 (PA3/ETH_MII_COL/ADC123_IN2(5T))
UART2_TX: JP1.4, U$1.25 (PA2/ETH_MDIO/ADC123_IN2(5T))
VCC: C1.2, IC2.3 (IN), JP1.1, JP2.1, U2.VBUS1 (VBUS)
VDD: C2.2, C3.2, IC1.1 (VIN), IC1.3 (VINH), IC2.2 (OUT), IC2.4 (OUT), R38.1, R40.2, R41.1, U$12.P$6 (6.VBAT), U$12.P$9 (9.VDD), U$12.P$11 (11.BS1)
VDDA: C10.2, C11.2, C12.2, C13.2, U$1.21 (VREF+), U$1.22 (VDDA), U$3.2 (2.OUT)

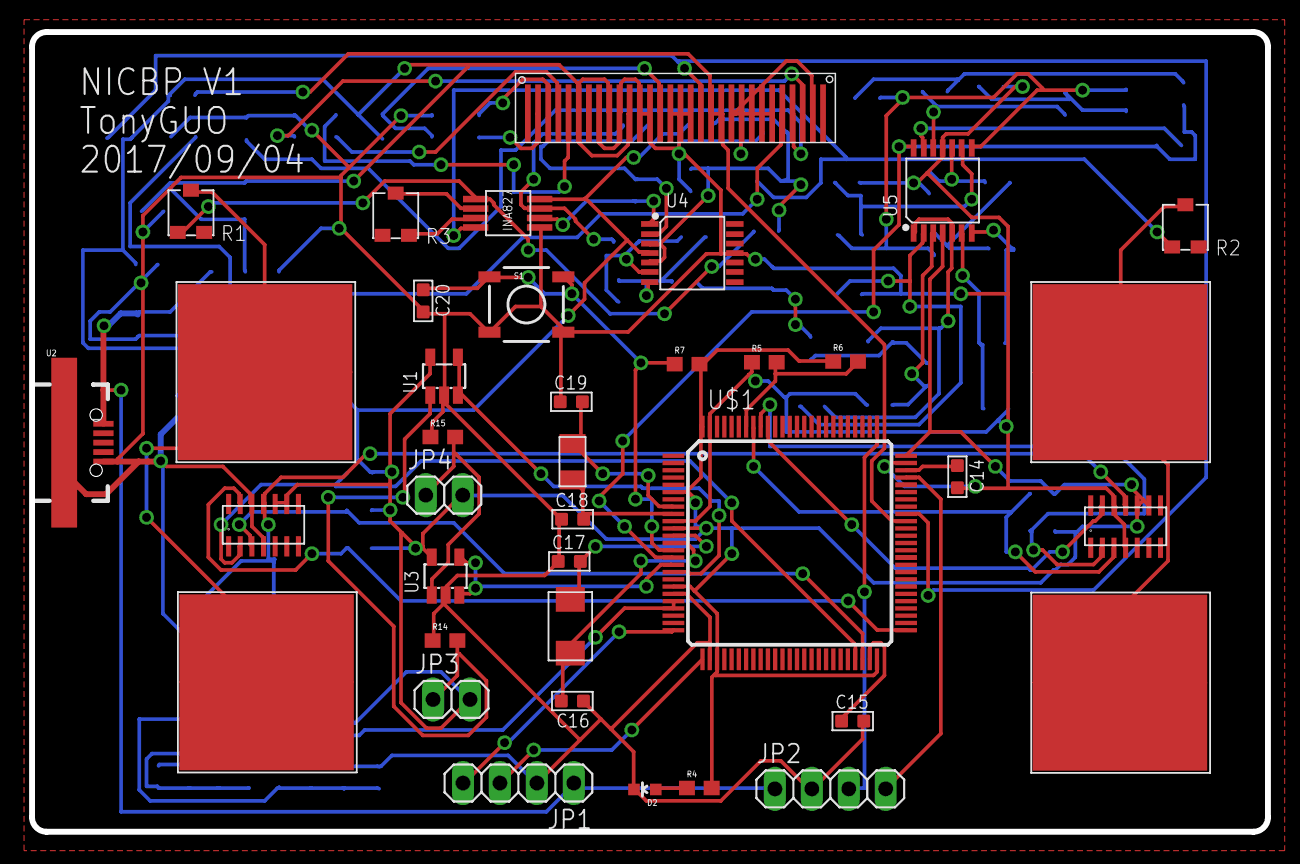
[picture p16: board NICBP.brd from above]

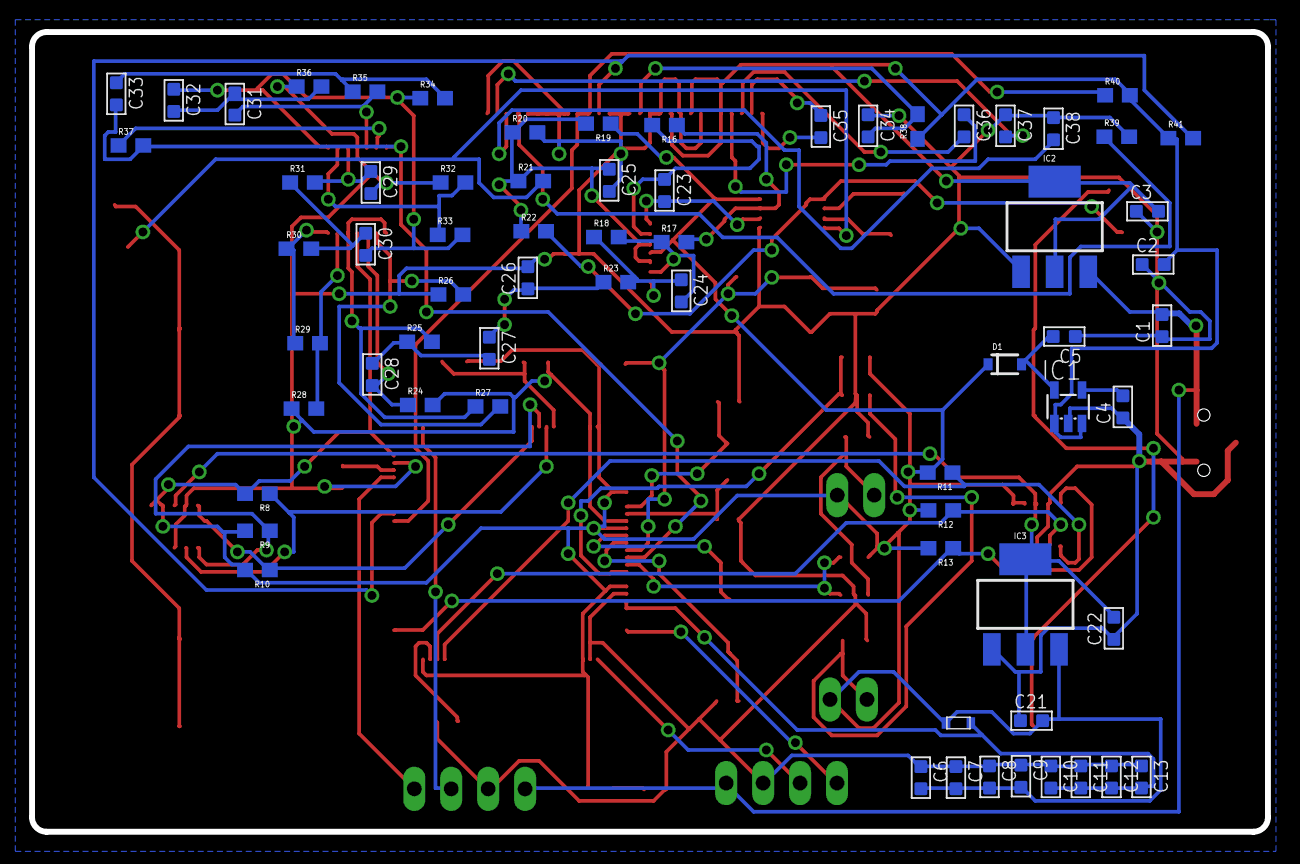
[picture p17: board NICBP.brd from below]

Board: 2 copper layers, 85.0 x 55.0 mm, 106 parts (68 on the bottom side), 69 nets.

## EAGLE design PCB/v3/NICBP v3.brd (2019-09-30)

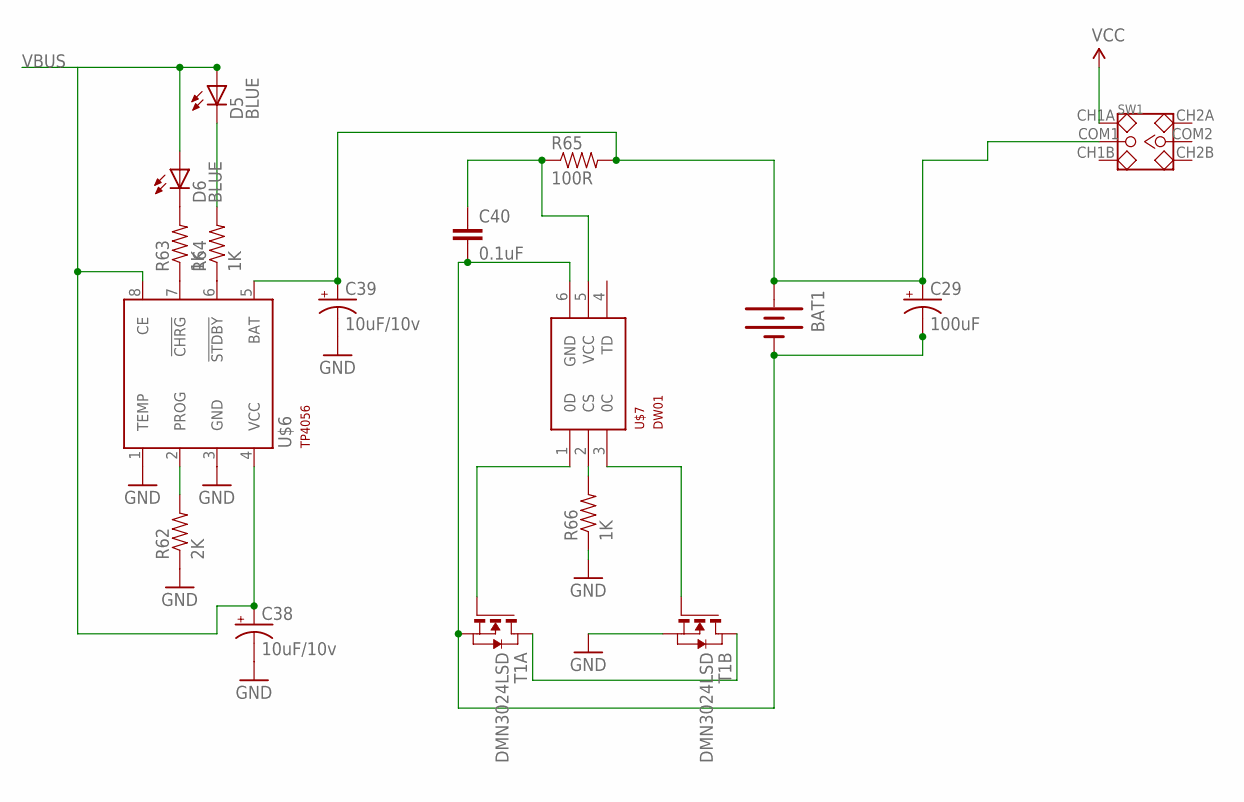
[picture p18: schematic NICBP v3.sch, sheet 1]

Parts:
BAT1: BATTERYLIPO-TABS; LIPO-110-TABS
C29: 100uF; NIPPON_F80
C38, C39: 10uF/10v; EIA3216-KIT
C40: 0.1uF; 0603-CAP
D5, D6: BLUE; LED-0603
R62: 2K; 0603-RES
R63, R64, R66: 1K; 0603-RES
R65: 100R; 0603-RES
SW1: SMD-TOGGLE-SWITCH-2CH(2X3P-7X3.5MM); SW6-2.54-SMD-7.0X3.5X1.5MM
T1: DMN3024LSD; TSSOP-8
U$6: TP4056; SOT23-8
U$7: DW01; SOT23-6

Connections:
GND: C38.C (-), C39.C (-), R62.1, R66.1, T1.6 (S), T1.7 (S), U$6.1 (TEMP), U$6.3 (GND); also elsewhere on the board
unnamed: BAT1.+, C29.+, C39.A (+), R65.2, SW1.COM1, U$6.5 (BAT)
unnamed: R62.2, U$6.2 (PROG)
unnamed: R63.1, U$6.7 (!CHRG)
unnamed: R64.1, U$6.6 (!STDBY)
unnamed: D6.C, R63.2
unnamed: D5.C, R64.2
unnamed: C40.1, R65.1, U$7.5 (VCC)
unnamed: BAT1.-, C29.-, C40.2, T1.2 (S), T1.3 (S), U$7.6 (GND)
unnamed: T1.4 (G), U$7.1 (0D)
unnamed: R66.2, U$7.2 (CS)
unnamed: T1.1 (D), T1.8 (D)
unnamed: T1.5 (G), U$7.3 (0C)
VBUS: C38.A (+), D5.A, D6.A, U$6.4 (VCC), U$6.8 (CE); also elsewhere on the board
VCC: SW1.CH1A; also elsewhere on the board

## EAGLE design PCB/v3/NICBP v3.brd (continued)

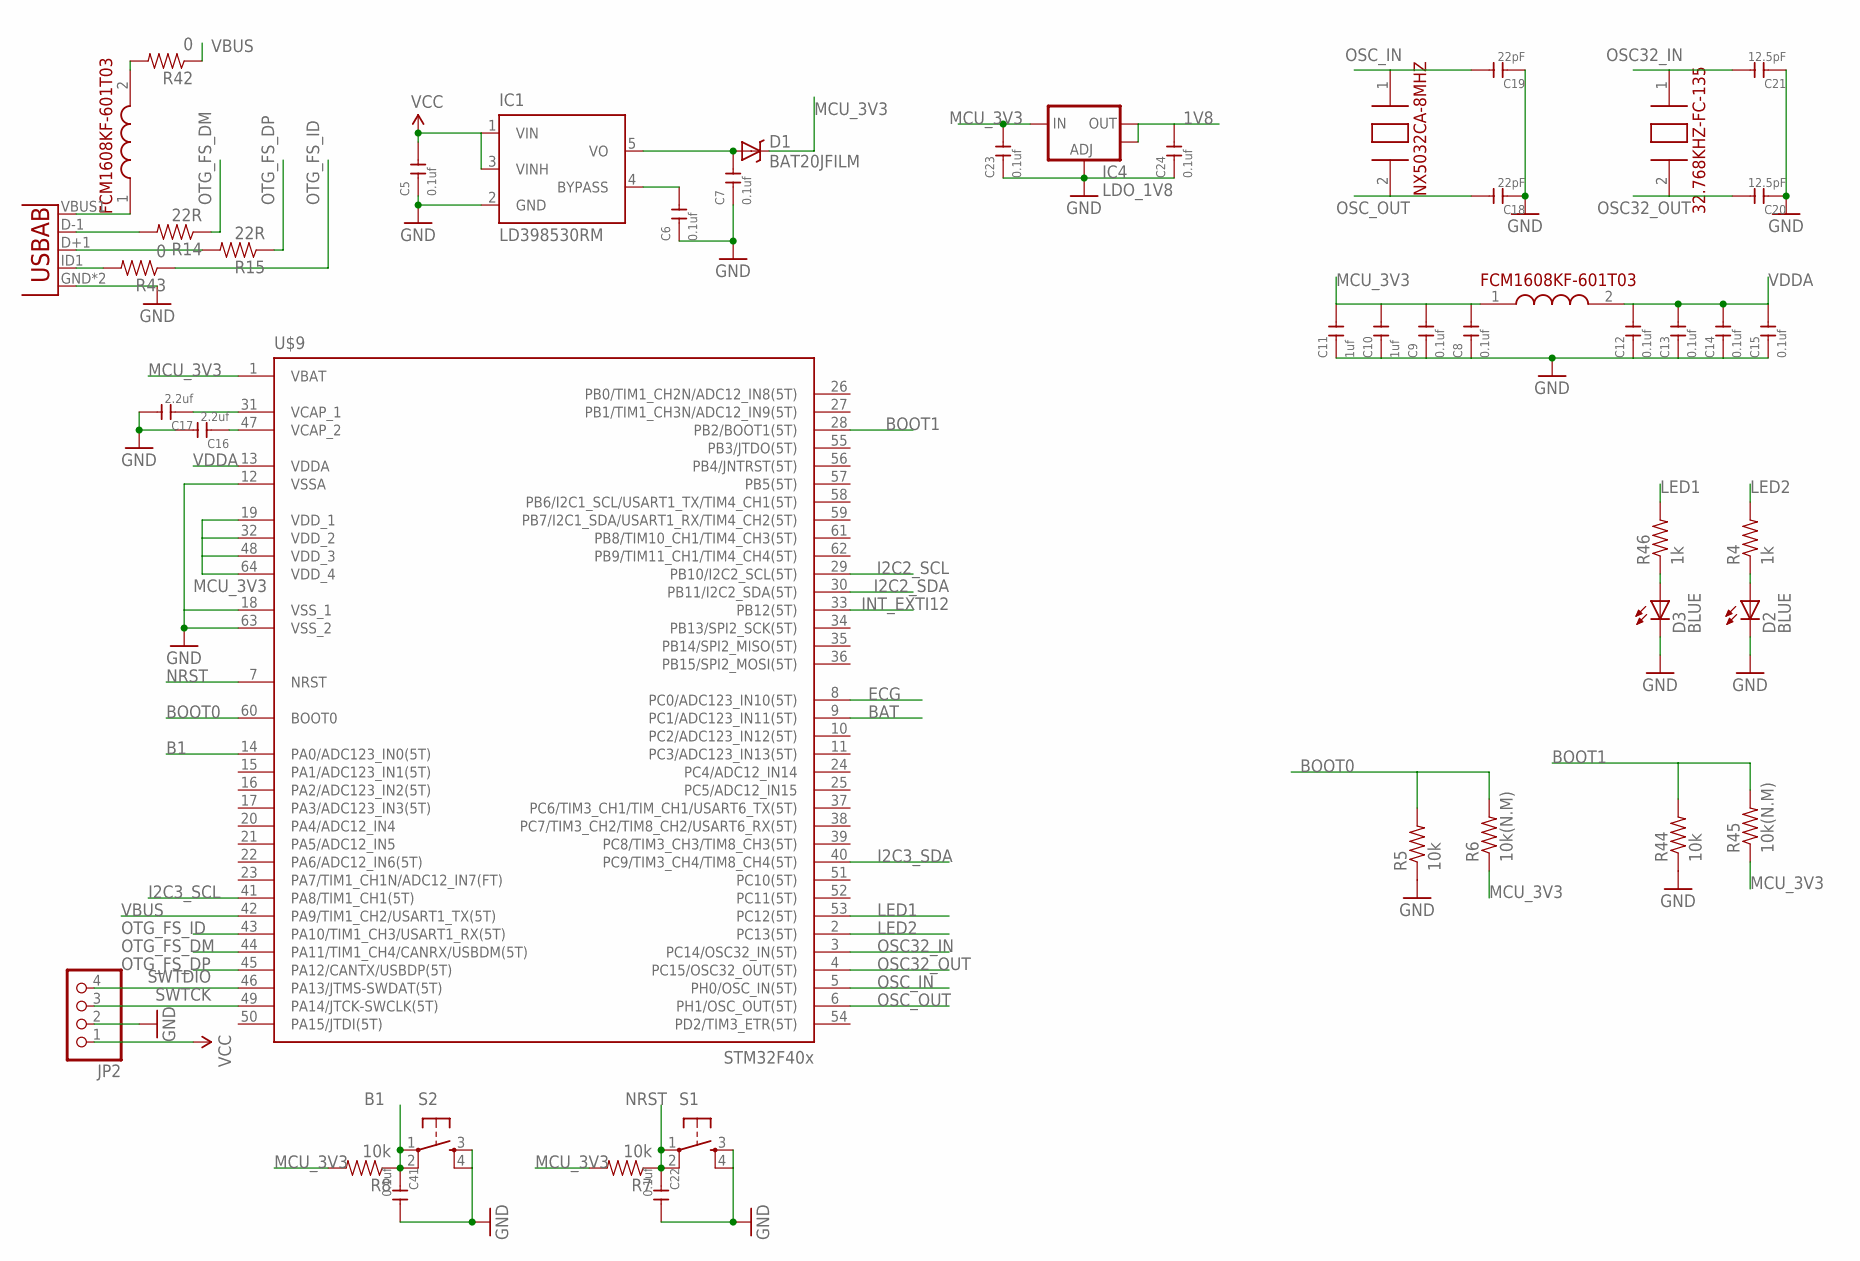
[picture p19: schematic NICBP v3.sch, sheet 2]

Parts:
C5, C6, C7, C8, C9, C12, C13, C14, C15, C22, C23, C24, C41: 0.1uf; C0603
C10, C11: 1uf; C0603
C16, C17: 2.2uf; C0603
C18, C19: 22pF; C0603
C20, C21: 12.5pF; C0603
D1: BAT20JFILM; SOD-323
D2, D3: BLUE; LED-0603
IC1: LD398530RM; SOT23-5L
IC4: LDO_1V8; SOT223
JP2: PINHD-1X4; 1X04
R4, R46: 1k; 0603
R5, R7, R8, R44: 10k; 0603
R6, R45: 10k(N.M); 0603
R14, R15: 22R; 0603-RES
R42, R43: 0; 0603-RES
S1, S2: TAC_SWITCHSMD; TACTILE_SWITCH_SMD
U1: USB""; USB-MICRO-SMD
U$2: NX5032CA-8MHZ
U$3, U$15: FCM1608KF-601T03
U$4: 32.768KHZ-FC-135
U$9: STM32F405R; TQFP64

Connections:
1V8: C24.2, IC4.2 (OUT), IC4.4 (OUT); also elsewhere on the board
B1: C41.1, R8.1, S2.1, S2.2, U$9.14 (PA0/ADC123_IN0(5T))
BAT: U$9.9 (PC1/ADC123_IN11(5T)); also elsewhere on the board
BOOT0: R5.2, R6.2, U$9.60 (BOOT0)
BOOT1: R44.2, R45.2, U$9.28 (PB2/BOOT1(5T))
ECG: U$9.8 (PC0/ADC123_IN10(5T)); also elsewhere on the board
GND: C5.1, C6.1, C7.1, C8.1, C9.1, C10.1, C11.1, C12.1, C13.1, C14.1, C15.1, C16.2, C17.2, C18.1, C19.1, C20.1, C21.1, C22.2, C23.1, C24.1, C41.2, D2.C, D3.C, IC1.2 (GND), IC4.1 (ADJ), JP2.2, R5.1, R44.1, S1.3, S1.4, S2.3, S2.4, U1.GND, U1.GND1 (GND), U$9.12 (VSSA), U$9.18 (VSS_1), U$9.63 (VSS_2); also elsewhere on the board
I2C2_SCL: U$9.29 (PB10/I2C2_SCL(5T)); also elsewhere on the board
I2C2_SDA: U$9.30 (PB11/I2C2_SDA(5T)); also elsewhere on the board
I2C3_SCL: U$9.41 (PA8/TIM1_CH1(5T)); also elsewhere on the board
I2C3_SDA: U$9.40 (PC9/TIM3_CH4/TIM8_CH4(5T)); also elsewhere on the board
INT_EXTI12: U$9.33 (PB12(5T)); also elsewhere on the board
LED1: R46.2, U$9.53 (PC12(5T))
LED2: R4.2, U$9.2 (PC13(5T))
MCU_3V3: C8.2, C9.2, C10.2, C11.2, C23.2, D1.1 (C), IC4.3 (IN), R6.1, R7.2, R8.2, R45.1, U$3.1 (1.IN), U$9.1 (VBAT), U$9.19 (VDD_1), U$9.32 (VDD_2), U$9.48 (VDD_3), U$9.64 (VDD_4); also elsewhere on the board
unnamed: D2.A, R4.1
unnamed: C17.1, U$9.31 (VCAP_1)
unnamed: C16.1, U$9.47 (VCAP_2)
unnamed: C6.2, IC1.4 (BYPASS)
unnamed: C7.2, D1.2 (A), IC1.5 (VO)
unnamed: R14.2, U1.D-1 (D-)
unnamed: R15.2, U1.D+1 (D+)
unnamed: R43.2, U1.ID1 (USBID)
unnamed: U1.VBUS1 (VBUS), U$15.1 (1.IN)
unnamed: R42.2, U$15.2 (2.OUT)
unnamed: D3.A, R46.1
NRST: C22.1, R7.1, S1.1, S1.2, U$9.7 (NRST)
OSC32_IN: C21.2, U$4.1 (1.XIN), U$9.3 (PC14/OSC32_IN(5T))
OSC32_OUT: C20.2, U$4.2 (2.XIN), U$9.4 (PC15/OSC32_OUT(5T))
OSC_IN: C19.2, U$2.1 (1.XIN), U$9.5 (PH0/OSC_IN(5T))
OSC_OUT: C18.2, U$2.2 (2.XOUT), U$9.6 (PH1/OSC_OUT(5T))
OTG_FS_DM: R14.1, U$9.44 (PA11/TIM1_CH4/CANRX/USBDM(5T))
OTG_FS_DP: R15.1, U$9.45 (PA12/CANTX/USBDP(5T))
OTG_FS_ID: R43.1, U$9.43 (PA10/TIM1_CH3/USART1_RX(5T))
SWTCK: JP2.3, U$9.49 (PA14/JTCK-SWCLK(5T))
SWTDIO: JP2.4, U$9.46 (PA13/JTMS-SWDAT(5T))
VBUS: R42.1, U$9.42 (PA9/TIM1_CH2/USART1_TX(5T)); also elsewhere on the board
VCC: C5.2, IC1.1 (VIN), IC1.3 (VINH), JP2.1; also elsewhere on the board
VDDA: C12.2, C13.2, C14.2, C15.2, U$3.2 (2.OUT), U$9.13 (VDDA)

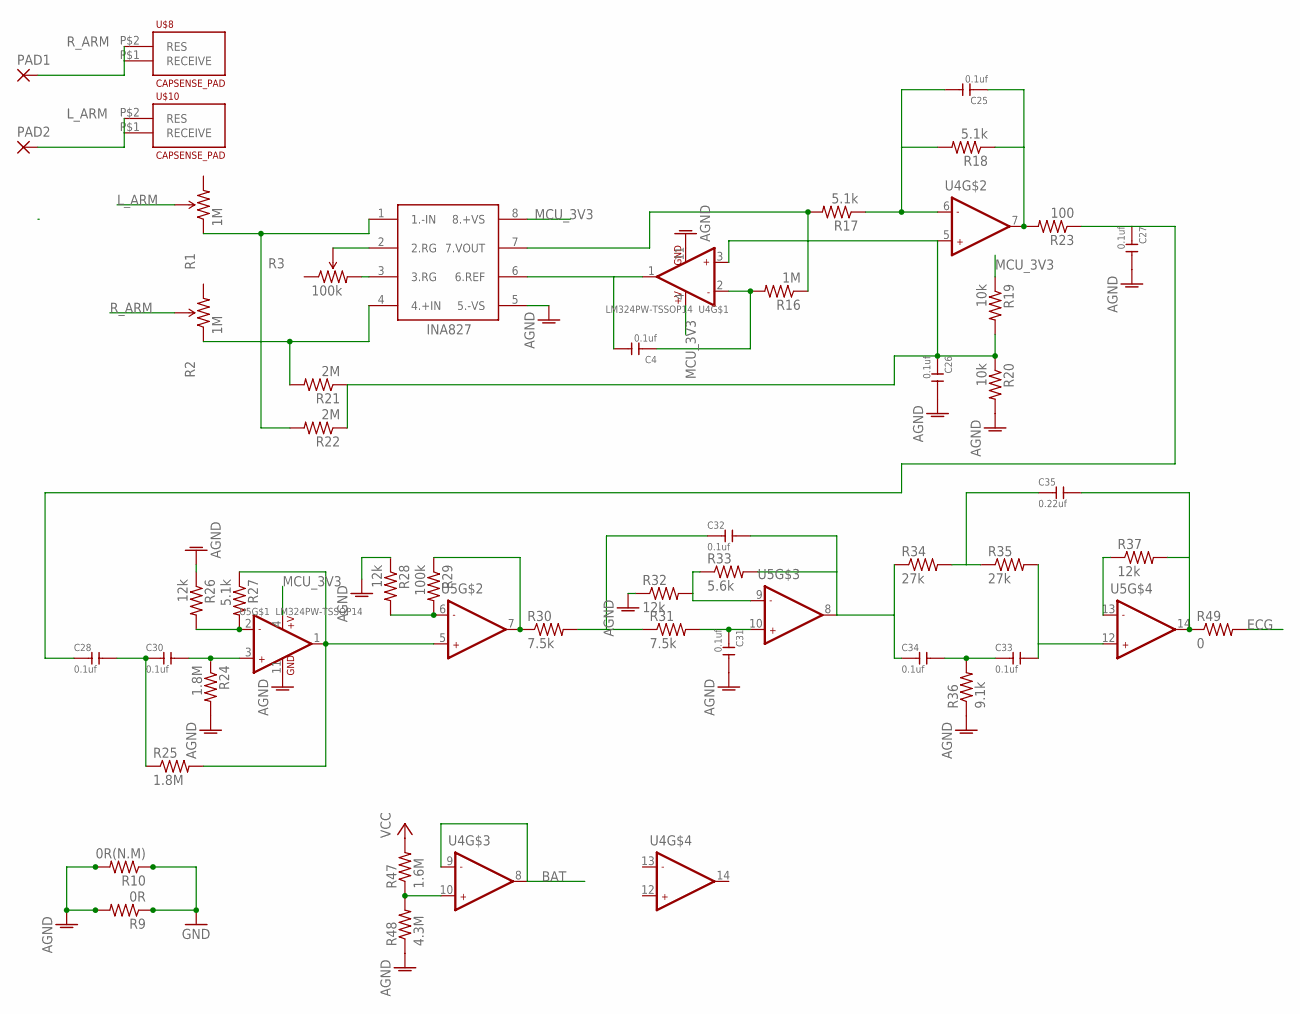
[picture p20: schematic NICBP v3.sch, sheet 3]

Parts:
C4, C25, C26, C27, C28, C30, C31, C32, C33, C34: 0.1uf; C0603
C35: 0.22uf; C0603
PAD1, PAD2: 3,17/1,3
R1, R2: 1M; TRIMPOT_TC33
R3: 100k; TRIMPOT_TC33
R9: 0R; 0603
R10: 0R(N.M); 0603
R16: 1M; 0603
R17, R18, R27: 5.1k; 0603
R19, R20: 10k; 0603
R21, R22: 2M; 0603
R23: 100; 0603
R24, R25: 1.8M; 0603
R26, R28, R32, R37: 12k; 0603
R29: 100k; 0603
R30, R31: 7.5k; 0603
R33: 5.6k; 0603
R34, R35: 27k; 0603
R36: 9.1k; 0603
R47: 1.6M; 0603
R48: 4.3M; 0603
R49: 0; 0603
U4, U5: LM324PW-TSSOP14; TSSOP14-0.65-5X4.4MM
U$5: INA827
U$8, U$10: CAPSENSE_PAD

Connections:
ADC1: C35.2, R37.2, R49.1, U5.14 (OUT2)
AGND: C26.2, C27.2, C31.2, R9.2, R10.2, R20.2, R24.2, R26.1, R28.1, R32.1, R36.1, R48.1, U4.11 (GND), U5.11 (GND), U$5.5 (5.-VS)
BAT: U4.8 (OUT2), U4.9 (-IN2); also elsewhere on the board
ECG: R49.2; also elsewhere on the board
GND: R9.1, R10.1; also elsewhere on the board
L_ARM: PAD2.1, R1.2 (WIPER), U$10.P$1 (RECEIVE), U$10.P$2 (RES)
MCU_3V3: R19.1, U4.4 (+V), U5.4 (+V), U$5.8 (8.+VS); also elsewhere on the board
unnamed: C27.1, C28.1, R23.1
unnamed: R47.1, R48.2, U4.10 (+IN2)
unnamed: R3.3 (CW), U$5.3 (3.RG)
unnamed: R3.2 (WIPER), U$5.2 (2.RG)
unnamed: R1.1 (CCW), R22.2, U$5.1 (1.-IN)
unnamed: R2.1 (CCW), R21.2, U$5.4 (4.+IN)
unnamed: C4.2, U4.1 (OUT1), U$5.6 (6.REF)
unnamed: C4.1, R16.2, U4.2 (-IN1)
unnamed: R16.1, R17.2, U$5.7 (7.VOUT)
unnamed: C25.2, R17.1, R18.2, U4.6 (-IN2)
unnamed: C25.1, R18.1, R23.2, U4.7 (OUT2)
unnamed: C26.1, R19.2, R20.1, R21.1, R22.1, U4.3 (+IN1), U4.5 (+IN2)
unnamed: R26.2, R27.2, U5.2 (-IN1)
unnamed: R25.2, R27.1, U5.1 (OUT1), U5.5 (+IN2)
unnamed: C30.2, R24.1, U5.3 (+IN1)
unnamed: C28.2, C30.1, R25.1
unnamed: R28.2, R29.2, U5.6 (-IN2)
unnamed: R29.1, R30.1, U5.7 (OUT2)
unnamed: C32.1, R30.2, R31.1
unnamed: C31.1, R31.2, U5.10 (+IN2)
unnamed: C32.2, C34.1, R33.2, R34.1, U5.8 (OUT2)
unnamed: R32.2, R33.1, U5.9 (-IN2)
unnamed: C35.1, R34.2, R35.1
unnamed: C33.1, C34.2, R36.2
unnamed: C33.2, R35.2, U5.12 (+IN2)
unnamed: R37.1, U5.13 (-IN2)
R_ARM: PAD1.1, R2.2 (WIPER), U$8.P$1 (RECEIVE), U$8.P$2 (RES)
VCC: R47.2; also elsewhere on the board


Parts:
C1: 0.1uf; C0603
C2, C36, C37: 1uf; C0603
C3: 4.7uf; C0603
R11, R12, R13, R40, R41: 4.7k; 0603
R38: 10k; 0603
R39: 390k; 0603
U$12: MAX30100
U$13: ER-OLED0.96

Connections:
1V8: U$12.11 (VDD); also elsewhere on the board
GND: C1.1, C3.1, C37.1, R39.2, U$12.4 (PGND), U$12.12 (GND), U$13.P$8 (8.VSS), U$13.P$10 (10.BS0), U$13.P$12 (12.BS2), U$13.P$13 (13.CS#), U$13.P$15 (15.D/C#), U$13.P$16 (16.R/W#), U$13.P$17 (17.E/RD#), U$13.P$21 (21.D3), U$13.P$22 (22.D4), U$13.P$23 (23.D5), U$13.P$24 (24.D6), U$13.P$25 (25.D7), U$13.P$29 (29.VLSS); also elsewhere on the board
I2C2_SCL: R11.1, U$12.2 (SCL); also elsewhere on the board
I2C2_SDA: R12.1, U$12.3 (SDA); also elsewhere on the board
I2C3_SCL: R41.2, U$13.P$18 (18.D0); also elsewhere on the board
I2C3_SDA: R40.1, U$13.P$19 (19.D1), U$13.P$20 (20.D2); also elsewhere on the board
INT_EXTI12: R13.1, U$12.13 (INT); also elsewhere on the board
MCU_3V3: R11.2, R12.2, R13.2, R40.2, R41.1, U$12.9 (R_LED+), U$12.10 (IR_LED+); also elsewhere on the board
unnamed: C1.2, R38.2, U$13.P$14 (14.RES#)
unnamed: C2.1, U$13.P$3 (3.C2N)
unnamed: C36.1, U$13.P$5 (5.C1N)
unnamed: C2.2, U$13.P$2 (2.C2P)
unnamed: C36.2, U$13.P$4 (4.C1P)
unnamed: R39.1, U$13.P$26 (26.IREF)
unnamed: C3.2, U$13.P$27 (27.VCOMH)
unnamed: C37.2, U$13.P$28 (28.VCC)
VCC: R38.1, U$13.P$6 (6.VBAT), U$13.P$9 (9.VDD), U$13.P$11 (11.BS1); also elsewhere on the board



Board: 2 copper layers, 97.2 x 71.3 mm, 125 parts (42 on the bottom side), 89 nets.

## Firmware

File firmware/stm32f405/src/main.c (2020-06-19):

#include <stdio.h>
#include <stdarg.h>
#include <stdbool.h>

#include <stm32f4xx.h>
#include <stm32f4xx_gpio.h>
#include <stm32f4xx_usart.h>
#include <stm32f4xx_exti.h>
#include <stm32f4xx_i2c.h>
#include <stm32f4xx_adc.h>
#include <stm32f4xx_rcc.h>
#include <stm32f4xx_dma.h>
#include <stm32f4xx_rtc.h>
#include <stm32f4xx_tim.h>

#include "adc.h"
#include "VCP.h"
#include "I2C.h"
#include "MAX3010x.h"
#include "SSD1306.h"

//#include "tiny_printf.h"
#include "stm32f4_fonts.h"

#define __FPU_PRESENT
#define __FPU_USED

volatile const uint32_t SECOND = 1000000;

volatile uint32_t TimingDelay;

volatile uint32_t micros = 0;

volatile uint32_t last_screen_update = 0;

enum{
   SPO2_SIGNAL_MODE = 1,
   SPO2_VALUE_MODE,
   ECG_SIGNAL_MODE
};
volatile bool clear_flag = false;
volatile uint32_t mode = SPO2_SIGNAL_MODE;

uint32_t ORG_IR = 0;
uint32_t ORG_RED = 0;
int32_t IRac = 0;
int32_t REDac = 0;
Filter_Data irf = {0};
Filter_Data redf = {0};   
uint32_t irACValueSqSum = 0;
uint32_t redACValueSqSum = 0;
uint16_t samplesRecorded = 0;
uint16_t pulsesDetected = 0;
uint32_t currentSaO2Value = 0;  

volatile uint32_t max_set_time = 0;
volatile int32_t max_value = 100;
volatile int32_t current_max = 100;

volatile uint32_t optical_read_time = 0;
volatile bool optical_ready = false;
volatile bool optical_process_flag = false;

int64_t map(int64_t x, int64_t in_min, int64_t in_max, int64_t out_min, int64_t out_max) {
   return (x - in_min) * (out_max - out_min) / (in_max - in_min) + out_min;
}

void Delay(__IO uint32_t nTime)
{
   TimingDelay = nTime;
   while(TimingDelay){
   }
}

void SysTick_Handler(void)
{
   if(TimingDelay){
      --TimingDelay;
   }
   ++micros;
}

void Init_LED()
{
   //Enable the GPIOD Clock
   RCC_AHB1PeriphClockCmd(RCC_AHB1Periph_GPIOC,ENABLE);


   // GPIOD Configuration
   GPIO_InitTypeDef GPIO_InitStruct;
   GPIO_InitStruct.GPIO_Pin = GPIO_Pin_12 | GPIO_Pin_13;
   GPIO_InitStruct.GPIO_Mode = GPIO_Mode_OUT;
   GPIO_InitStruct.GPIO_Speed = GPIO_Speed_50MHz;
   GPIO_InitStruct.GPIO_OType = GPIO_OType_PP;
   GPIO_InitStruct.GPIO_PuPd = GPIO_PuPd_UP;

   //GPIO_SetBits(GPIOC, GPIO_Pin_12);
   //GPIO_SetBits(GPIOC, GPIO_Pin_13);
   GPIO_Init(GPIOC, &GPIO_InitStruct);   
}

void EXTILine0_Config(void)
{
   EXTI_InitTypeDef   EXTI_InitStructure;
   GPIO_InitTypeDef   GPIO_InitStructure;
   NVIC_InitTypeDef   NVIC_InitStructure;

   /* Enable GPIOB clock */
   RCC_AHB1PeriphClockCmd(RCC_AHB1Periph_GPIOA, ENABLE);
   /* Enable SYSCFG clock */
   RCC_APB2PeriphClockCmd(RCC_APB2Periph_SYSCFG, ENABLE);

   /* Configure PB0 pin as input floating */
   GPIO_InitStructure.GPIO_Mode = GPIO_Mode_IN;
   GPIO_InitStructure.GPIO_PuPd = GPIO_PuPd_NOPULL;
   GPIO_InitStructure.GPIO_Pin = GPIO_Pin_0;
   GPIO_Init(GPIOA, &GPIO_InitStructure);

   /* Connect EXTI Line0 to PB0 pin */
   SYSCFG_EXTILineConfig(EXTI_PortSourceGPIOA, EXTI_PinSource0);

   /* Configure EXTI Line0 */
   EXTI_InitStructure.EXTI_Line = EXTI_Line0;
   EXTI_InitStructure.EXTI_Mode = EXTI_Mode_Interrupt;
   EXTI_InitStructure.EXTI_Trigger = EXTI_Trigger_Falling;  
   EXTI_InitStructure.EXTI_LineCmd = ENABLE;
   EXTI_Init(&EXTI_InitStructure);

   /* Enable and set EXTI Line0 Interrupt to the lowest priority */
   NVIC_InitStructure.NVIC_IRQChannel = EXTI0_IRQn;
   NVIC_InitStructure.NVIC_IRQChannelPreemptionPriority = 1;
   NVIC_InitStructure.NVIC_IRQChannelSubPriority = 1;
   NVIC_InitStructure.NVIC_IRQChannelCmd = ENABLE;
   NVIC_Init(&NVIC_InitStructure);
}

void EXTILine15_10_Config(void)
{
   EXTI_InitTypeDef   EXTI_InitStructure;
   GPIO_InitTypeDef   GPIO_InitStructure;
   NVIC_InitTypeDef   NVIC_InitStructure;

   /* Enable GPIOB clock */
   RCC_AHB1PeriphClockCmd(RCC_AHB1Periph_GPIOB, ENABLE);
   /* Enable SYSCFG clock */
   RCC_APB2PeriphClockCmd(RCC_APB2Periph_SYSCFG, ENABLE);

   /* Configure PB0 pin as input floating */
   GPIO_InitStructure.GPIO_Mode = GPIO_Mode_IN;
   GPIO_InitStructure.GPIO_PuPd = GPIO_PuPd_NOPULL;
   GPIO_InitStructure.GPIO_Pin = GPIO_Pin_12;
   GPIO_Init(GPIOB, &GPIO_InitStructure);

   /* Connect EXTI Line0 to PB0 pin */
   SYSCFG_EXTILineConfig(EXTI_PortSourceGPIOB, EXTI_PinSource12);

   /* Configure EXTI Line0 */
   EXTI_InitStructure.EXTI_Line = EXTI_Line12;
   EXTI_InitStructure.EXTI_Mode = EXTI_Mode_Interrupt;
   EXTI_InitStructure.EXTI_Trigger = EXTI_Trigger_Falling;  
   EXTI_InitStructure.EXTI_LineCmd = ENABLE;
   EXTI_Init(&EXTI_InitStructure);

   /* Enable and set EXTI Line0 Interrupt to the lowest priority */
   NVIC_InitStructure.NVIC_IRQChannel = EXTI15_10_IRQn;
   NVIC_InitStructure.NVIC_IRQChannelPreemptionPriority = 1;
   NVIC_InitStructure.NVIC_IRQChannelSubPriority = 0;
   NVIC_InitStructure.NVIC_IRQChannelCmd = ENABLE;
   NVIC_Init(&NVIC_InitStructure);
}

void MAX3010x_SignalProcess()
{
   Read_MAX3010x();

   ORG_IR = IR;
   ORG_RED = RED;

   IRac = DCRemove(IR,&IRcw);
   REDac = DCRemove(RED,&REDcw);

   IRac = MeanDiff(IRac);
   REDac = MeanDiff(REDac);

   IRac = LowPassButterworthFilter(IRac,&irf);
   REDac = LowPassButterworthFilter(REDac,&redf);


   irACValueSqSum += IRac * IRac;
   redACValueSqSum += REDac * REDac;
   samplesRecorded++;  
   if(/*detectPulse(IRac)*/true){
      pulsesDetected++;


      float red_log_rms = log( sqrt(redACValueSqSum/samplesRecorded) );
      float ir_log_rms = log( sqrt(irACValueSqSum/samplesRecorded) );
      float ratioRMS = 0.0f;
      if(red_log_rms != 0.0f && ir_log_rms != 0.0f){
	 ratioRMS = red_log_rms / ir_log_rms;
      }
      currentSaO2Value = 110.0f - 14.0f * ratioRMS;	// SPo2 value by pulse-rate
      if(currentSaO2Value > 99){currentSaO2Value = 99;}
      else if(currentSaO2Value < 70){currentSaO2Value = 70;}


      if(pulsesDetected % RESET_SPO2_EVERY_N_PULSES == 0){
	 irACValueSqSum = 0;
	 redACValueSqSum = 0;
	 samplesRecorded = 0;
      }     
   }


   BalanceIntesities();   
}

int main(void)
{
   if(SysTick_Config(SystemCoreClock / 1000 / 1000)){
      while(1){}
   }

   EXTILine15_10_Config();
   Delay(5000);
   EXTILine0_Config();
   Delay(5000);

   USBVCPInit();
   Delay(5000);

   Init_MAX3010x();
   Delay(5000);
   MAX3010x_SignalProcess();
   Delay(5000);
   Init_I2C3();
   Delay(5000);
   Init_SSD1306();
   Delay(5000);

   //Init_ADC();
   ADC_4_Channel_Init();
   Init_LED();

   __IO uint32_t HSEStatus = 0;
   HSEStatus = RCC->CR & RCC_CR_HSERDY;
   if(HSEStatus){
      GPIO_SetBits(GPIOC, GPIO_Pin_12);
   }
   else{
      GPIO_ResetBits(GPIOC, GPIO_Pin_12);
   }   

   SSD1306_Fill(0x00);
   SSD1306_UpdateScreen();
   Delay(SECOND);
   SSD1306_Fill(0xFF);
   SSD1306_UpdateScreen();
   Delay(SECOND);
   SSD1306_Fill(0x00);
   SSD1306_UpdateScreen();  
   Delay(SECOND);   

   SSD1306_GotoXY(3, 4);
   SSD1306_Puts("NICBP v2", &Font_11x18, 0xFF);
   SSD1306_GotoXY(3, 25);
   SSD1306_Puts("20190817", &Font_11x18, 0xFF);
   SSD1306_GotoXY(3, 45);
   SSD1306_Puts("TonyGUO", &Font_11x18, 0xFF);
   SSD1306_UpdateScreen();  
   Delay(SECOND);
   SSD1306_Fill(0x00);
   SSD1306_UpdateScreen();

   int id_state = 0;
   int recheck_state = 0;
   int sn = 1;  

   uint16_t idx = 0;
   uint16_t lx = 0,ly = 63;

   bool blue_flag = false;
   while(1){
      if(blue_flag){
	 GPIO_SetBits(GPIOC, GPIO_Pin_13);
      }
      else{
	 GPIO_ResetBits(GPIOC, GPIO_Pin_13);
      }  
/*
      if((micros - optical_read_time) > 20000){
	 optical_read_time = micros;
	 optical_ready = true;
      }
*/
      if(USB_VCP_GetStatus() == USB_VCP_CONNECTED){
	 if(micros - last_screen_update > SECOND){
	    char str[255] = "";
	    SSD1306_GotoXY(20, 25);
	    SSD1306_Puts("USB Mode", &Font_11x18, 0xFF);	    
	    SSD1306_UpdateScreen();
	    last_screen_update = micros;
	 }

	 if(sn == 1){
	    uint8_t c;
	    if (USB_VCP_Getc(&c) == USB_VCP_DATA_OK) {
	       /* Return data back */
	       //TM_USB_VCP_Putc(c);
	       if(c == 'A' && id_state == 0){
		  ++id_state;
	       }
	       if(c == 'C' && id_state == 1){
		  ++id_state;
	       }
	       if(c == 'K' && id_state == 2){
		  ++id_state;
		  USB_VCP_Puts("ACK");
		  sn = 0;

	       }
	    }
	 }
	 else{
	    uint8_t c;
	    if (USB_VCP_Getc(&c) == USB_VCP_DATA_OK) {
	       /* Return data back */
	       //TM_USB_VCP_Putc(c);
	       if(c == 'G' && recheck_state == 0){
		  ++recheck_state;
	       }
	       if(c == 'O' && recheck_state == 1){
		  ++recheck_state;
	       }
	       if(c == 'T' && recheck_state == 2){
		  ++recheck_state;
		  USB_VCP_Puts("GOT");
	       }
	    }
	 }

	 if(recheck_state == 3){
	    if(ADC3_ready){
	       ADC3_ready = false;
	       unsigned char str[255] = {0};
	       //sprintf(str,"R%4d,%4d,%4d,%4d,%4d,",micros,ADC3_value[0],ADC3_value[1],ADC3_value[2],ADC3_value[3]);
	       sprintf(str,"D%4d,%6d,%6d, \n",ADC3_value[0],ORG_IR,ORG_RED);
	       USB_VCP_Puts(str);
	       if(optical_ready){
		  optical_ready = false;
		  MAX3010x_SignalProcess();
	       }	       
	    } 
	    //else if(optical_ready/*Read_MAX30100_INT()*/){
	    //   optical_ready = false;
	    //   MAX3010x_SignalProcess();
	       /*
		  unsigned char str[255];
		  sprintf(str,"O%6d, \n",RED);
		  USB_VCP_Puts(str);*/
	    //}
	 }
	 blue_flag ^= true;
      }
      else{
	 if(mode == SPO2_SIGNAL_MODE){

	    MAX3010x_SignalProcess();

	    if( (micros - max_set_time) > (SECOND * 1.5f)){
	       max_set_time = micros;
	       max_value = current_max;
	       current_max = 100;
	    }
	    else{
	       if(abs(REDac) > current_max){
		  current_max = REDac;
	       }
	    }	 

	    if(clear_flag){
	       SSD1306_Fill(0x00);
	       SSD1306_UpdateScreen();
	       clear_flag = false;

	       idx = 0;
	       lx = 0,ly = 63;	    
	    }
	    if(idx >= 128){
	       SSD1306_LeftRolling();
	       SSD1306_DrawLine(126,ly,127,map(REDac,-max_value,max_value,0,63),0xFF);
	       ly = map(REDac,-max_value,max_value,0,63);
	       SSD1306_UpdateScreen();
	    }
	    else{
	       SSD1306_DrawLine(lx,ly,idx,map(REDac,-max_value,max_value,0,63),0xFF);
	       lx = idx;ly = map(REDac,-max_value,max_value,0,63);
	       SSD1306_UpdateScreen();
	       ++idx;
	    }      
	 }
	 else if(mode == SPO2_VALUE_MODE){  

	    MAX3010x_SignalProcess();

	    if(clear_flag){
	       SSD1306_Fill(0x00);
	       SSD1306_UpdateScreen();
	       clear_flag = false;
	    }	 

	    unsigned char spo2_str[255];
	    sprintf(spo2_str,"SpO2 : %2d",currentSaO2Value);
	    SSD1306_GotoXY(3, 25);
	    SSD1306_Puts(spo2_str, &Font_11x18, 0xFF);
	    SSD1306_UpdateScreen();

	 }
	 else if(mode == ECG_SIGNAL_MODE && ADC3_ready){
	    ADC3_ready = false;
	    if( (micros - max_set_time) > (SECOND * 1.5f)){
	       max_set_time = micros;
	       max_value = current_max;
	       current_max = 100;
	    }
	    else{
	       if(ADC3_value[0] > current_max){
		  current_max = ADC3_value[0];
	       }
	    }		 
	    if(clear_flag){
	       SSD1306_Fill(0x00);
	       SSD1306_UpdateScreen();
	       clear_flag = false;

	       idx = 0;
	       lx = 0,ly = 63;	    
	    }	 
	    if(idx >= 128){
	       SSD1306_LeftRolling();
	       SSD1306_DrawLine(126,ly,127,map(ADC3_value[0],-max_value,max_value,0,63),0xFF);
	       ly = map(ADC3_value[0],-max_value,max_value,0,63);
	       SSD1306_UpdateScreen();
	    }
	    else{
	       SSD1306_DrawLine(lx,ly,idx,map(ADC3_value[0],-max_value,max_value,0,63),0xFF);
	       lx = idx;ly = map(ADC3_value[0],-max_value,max_value,0,63);
	       SSD1306_UpdateScreen();
	       ++idx;
	    }  	 
	 }

      }
   }

   return(0); // System will implode
}    

void EXTI0_IRQHandler(void)
{
   if(EXTI_GetITStatus(EXTI_Line0) != RESET){
      ++mode;
      if(mode > ECG_SIGNAL_MODE){
	 mode = SPO2_SIGNAL_MODE;
      }
   }

   clear_flag = true;

   EXTI_ClearITPendingBit(EXTI_Line0);
   EXTI_ClearFlag(EXTI_Line0);
}

void EXTI15_10_IRQHandler(void)
{
   if(EXTI_GetITStatus(EXTI_Line12) != RESET){
      optical_ready = true;
   }

   EXTI_ClearITPendingBit(EXTI_Line12);
   EXTI_ClearFlag(EXTI_Line12);   
}

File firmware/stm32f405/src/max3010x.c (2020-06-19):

#include "max3010x.h"

int32_t IRcw = 0;
int32_t REDcw = 0;

uint32_t IR = 0;
uint32_t RED = 0;

uint8_t redLEDCurrent = 5;


int32_t msum = 0;
int32_t mvalues[MEAN_FILTER_SIZE];
int32_t mindex = 0;
int32_t mcount = 0;

volatile uint32_t lastREDLedCurrentCheck = 0;

#if defined(_MAX30102_)
uint32_t decay_counter = 0;
const double decay_coeff = -0.31415;
#endif

uint8_t currentPulseDetectorState = PULSE_IDLE;
uint32_t lastBeatThreshold = 0;
uint32_t currentBPM;
uint32_t valuesBPM[PULSE_BPM_SAMPLE_SIZE] = {0};
uint32_t valuesBPMSum = 0;
uint8_t valuesBPMCount = 0;
uint8_t bpmIndex = 0;

void Init_I2C2()
{
    GPIO_InitTypeDef GPIO_InitStructure;
    I2C_InitTypeDef I2C_InitStruct;

    RCC_APB1PeriphClockCmd(RCC_APB1Periph_I2C2, ENABLE);
    RCC_AHB1PeriphClockCmd(RCC_AHB1Periph_GPIOB, ENABLE);

    GPIO_InitStructure.GPIO_Pin = GPIO_Pin_10 | GPIO_Pin_11;
    GPIO_InitStructure.GPIO_Mode = GPIO_Mode_AF;
    GPIO_InitStructure.GPIO_Speed = GPIO_Speed_100MHz;
    GPIO_InitStructure.GPIO_OType = GPIO_OType_OD;
    GPIO_InitStructure.GPIO_PuPd  = GPIO_PuPd_UP;
    GPIO_Init(GPIOB, &GPIO_InitStructure);

    GPIO_PinAFConfig(GPIOB, GPIO_PinSource10, GPIO_AF_I2C2);
    GPIO_PinAFConfig(GPIOB, GPIO_PinSource11, GPIO_AF_I2C2);

    I2C_InitStruct.I2C_ClockSpeed = 100000;
    I2C_InitStruct.I2C_Mode = I2C_Mode_I2C;
    I2C_InitStruct.I2C_DutyCycle = I2C_DutyCycle_2;
    I2C_InitStruct.I2C_OwnAddress1 = 0x00;
    I2C_InitStruct.I2C_Ack = I2C_Ack_Enable;
    I2C_InitStruct.I2C_AcknowledgedAddress = I2C_AcknowledgedAddress_7bit;
    I2C_Init(I2C2, &I2C_InitStruct);

    I2C_Cmd(I2C2, ENABLE);
}

#if defined(_MAX30100_)
void Init_MAX30100()
{
   I2C_Write(I2C2,MAX30100_ADDRESS,MAX30100_MODE_CONFIG, 0x40);
   Delay(5000);
   I2C_Write(I2C2,MAX30100_ADDRESS,MAX30100_MODE_CONFIG,MAX3010x_MODE_SPO2_HR);
   Delay(5000);
   I2C_Write(I2C2,MAX30100_ADDRESS,MAX30100_INT_ENABLE, 0x10);
   Delay(5000);
   I2C_Write(I2C2,MAX30100_ADDRESS,MAX30100_LED_CONFIG,(i27 << 4) | FIX_IR_CURRENT);
   Delay(5000);
   I2C_Write(I2C2,MAX30100_ADDRESS,MAX30100_SPO2_CONFIG,(sr100<<2) | pw1600);
   Delay(5000);
   I2C_Write(I2C2,MAX30100_ADDRESS,MAX30100_FIFO_WR_PTR,0x00);
   I2C_Write(I2C2,MAX30100_ADDRESS,MAX30100_OVRFLOW_CTR,0x00);
   I2C_Write(I2C2,MAX30100_ADDRESS,MAX30100_FIFO_RD_PTR,0x00);
/*
      I2C_start(I2C2, MAX30100_ADDRESS, I2C_Direction_Transmitter); 
      I2C_write(I2C2, MAX30100_INT_ENABLE); 
      I2C_stop(I2C2); 
      I2C_start(I2C2, MAX30100_ADDRESS, I2C_Direction_Receiver);
      uint8_t int_data;
      int_data = I2C_read_nack(I2C2);
      I2C_stop(I2C2);
      I2C_Write(I2C2,MAX30100_ADDRESS,MAX30100_INT_ENABLE,int_data | 0x10);
      */

}
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

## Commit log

2018-10-02 Circuit and Layout Eagle project
    [NICBP.brd, NICBP.sch]
2019-08-23 NICBP v1
    [NICBP.brd, NICBP.sch]
2019-09-30 version 3 Reduce parts and USB-FS VCP
    [NICBP v3.brd, NICBP v3.sch]
2020-06-17 move to PCB
    [NICBP v3.brd, NICBP v3.sch, NICBP.brd, NICBP.sch]
2020-06-21 add ECG Board Reference Design
    [ECG.brd, ECG.sch, two electrode ECG.brd, two electrode ECG.sch]

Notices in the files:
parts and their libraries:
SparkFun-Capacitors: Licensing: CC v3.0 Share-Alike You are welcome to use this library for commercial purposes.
